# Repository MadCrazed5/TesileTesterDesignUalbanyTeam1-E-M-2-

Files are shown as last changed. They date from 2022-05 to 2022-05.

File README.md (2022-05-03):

# TesileTesterDesignUalbanyTeam1(E+M^2)
 Tesile Tester System Design

**Repository Contents**
This repository holds the STL files,Arduino libraries,Source code and Matlab application used in this Design. This repository also holds the physical design and the experimental results of this design.

**System Parts** (Refer to STL Directory For 3D printed Materials and Misc Directory for Physical Parts (Instructions and Materials document)
Wingnut 4x -  .55cm (diameter)
Big Phillips head  2x - .5 cm (diameter) - 3.1 cm (length)
Nut 2x - .65 cm (diameter)
Small Phillips 4x - .3cm (diameter) - 2.45 cm (length)
Plastic Washer 2x - .55cm(diameter) - .65cm(length)
Flat Phillips 2x - 8x1.5 inch 
Metal Washers 2x- .5 cm(diameter)
Sheet Metal Screws 12x - 8x1 inch
3D printed Rails 6x
3D printed Handle Set 1x
3D printed Brick 1x
3D printed Washers 2x
3D printed Clamps 2x
3D printed “Feet” 4x
Pulling Winch 1x 
------->https://www.amazon.com/dp/B001AJBP04?psc=1&ref=ppx_yo2ov_dt_b_product_details
Abrasion Proof Rope 1x - about 3 Feet 
 VL53L1X Laser Distance Sensor 1x 
 -------> https://www.amazon.com/Sinkr-VL53L1X-Maximum-Distance-Flight/dp/B09J7TDZ4B/ref=sr_1_1_sspa?camp=1789&creative=9325&keywords=VL53L1X&linkCode=ur2&linkId=9e15f283771ade0247e76342a71cef3f&qid=1648139371&sr=8-1-spons&spLa=ZW5jcnlwdGVkUXVhbGlmaWVyPUEyQ0QxS1A4Q0JXMklQJmVuY3J5cHRlZElkPUEwNjMwMjk1Mk1YWUxKTUhXNUtIRCZlbmNyeXB0ZWRBZElkPUEwNzg5NTUwMko0T1dGSEtMQTkwRyZ3aWRnZXROYW1lPXNwX2F0ZiZhY3Rpb249Y2xpY2tSZWRpcmVjdCZkb05vdExvZ0NsaWNrPXRydWU&th=1
 
**Software Dependencies**
Refer to Ardunio Libraries folder

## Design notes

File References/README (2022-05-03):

**MatLab References**
https://www.mathworks.com/

**Arduino References** 

Load Cell Code
-----> https://www.instructables.com/Arduino-Scale-With-5kg-Load-Cell-and-HX711-Amplifi/?amp_page=true

Laser Sensor Code
-----> https://learn.sparkfun.com/tutorials/qwiic-distance-sensor-vl53l1x-hookup-guide/arduino-example-code

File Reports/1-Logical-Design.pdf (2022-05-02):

PP-2017 V2.1

ANALYSIS & LOGICAL DESIGN | 1

# Logical Design Proposal Improving the Ultimate Tensile Strength Team One

Maduabuchi Okolo, Maria Peregrina, Ethan Wrobel

Activity Report

Abstract—Based upon the original design of the tensiometer, issues were encountered that inhibited the process to calculate a stress-strain curve. Therefore, by replacing the clamps and adding a winch, the system would improve drastically. The original clamps that were given lowered the amount of time you can measure force in a given amount of time, due to how long it takes to actually put the material within said clamps. Thus, 3-D printed clamps that make the process of measuring the material easier. Same thing can be said about the original pulley system. Originally someone would have to pull on the rope manually to allow force to be measured and to stretch the material, but this leads to inaccuracy due to many factors like pulling the rope too fast. So, by adding a winch to the design, it allows us to stretch the material with a rope at a more constant speed that can be replicated. Once, these improvements are made, the next step would be to find the median of the load and distance data. This will be done by improving the program that is used to help compute the stress-strain curve.

Index Terms—Uniaxial Tensiometer, System Analysis, Engineering Design

✦

### 1 BACKGROUND

WHILE using the Ultimate Tensile Strength Tester there were some issues that arose. Such issues were: the tensiometer clamps, accurately of the distance which is due to the ultrasonic proximity sensor. In order to test the system with some real material, like nitrile medical gloves we need to open the tensiometer clamps to place the material between them. However, screwing open and securing the material in the tensiometer clamps wasn’t user friendly and also time consuming when doing various trials. Once the material was placed between the tensiometer clamps, the material was stretched to collect data. The data was skewed and once the material broke, the ultrasonic proximity

- Maduabuchi Okolo,
E-mail:mokolo@albany.edu,
- Maria Peregrina,
E-mail: mperegrina@albany.edu,
- Ethan Wrobel,
E-mail: ewrobel@albany.edu, University at Albany.

sensor was displaying inaccurate data. In order to improve on these issues, we decided to change the tensiometer clamps.There were some limitations in this solution, because when searching for clamps there weren’t an existing solutions on the market. The clamps were either to big, or didn’t have teeth to hold the material. Therefore, we decided to 3D-print our own design of a tensiometer clamp. This improvement will benefit the project stakeholders by making the system user friendly. Another improvement we will implement is including a mini winch which will be used to pull the rope. This will help improve the accuracy of the ultrasonic proximity sensor by eliminating human error when pulling the rope. Data accurately and precision is the most important aspects therefore benefit the customer using the system.Some limitations in this solution were being able to find a mini winch on the market that fits the dimensions of our system and is within our budget.

Activity Report

2 | ANALYSIS & LOGICAL DESIGN

### 2 SYSTEM REQUIREMENTS & CON-

STRAINTS
Figure 1 depicts the system use cases discussed in class. In this section, define requirements that your proposed system addresses. See the constraints section (Section 2.3) for nonfunctional system requirements that have already been defined in class. This section should focus on functional requirements. It is critical here that you prioritize requirements that are the most important to the stakeholder. These are the requirements that your proposed idea should be improving. For each requirement, summarize the required functionality in detail. Use subsections to organize this information.

### 2.1 Requirement #1 Simple Clamps

This clamp will hold onto the User’s material. The User must use a screw driver, the two pieces of the clamp and the material they are testing to interact with the clamp. The User needs to separate the two parts of a clamp with a screw driver(flat head or corkscrew), then place the material in between the ”teeth” of the two parts of the clamp. Afterwards, the User must use the screwdriver to hold the two parts of the clamp with the material in between. These actions are performed twice in total for each edge of the material. The User will see two clamps screwed onto the machine. The clamp they see will have one part that is long and is directly screwed onto the machine. The other part of the clamp is screwed onto the first part the clamp.
Normal Flow
To Secure material to the clamps
- Step #1: Remove screws from clamps
- Step #2: Place material within clamps
- Step #3: Screw clamps back together to secure material
Alternative Flow
Material slips through clamp
- Step #1: Unscrew clamps again
- Step #2: Place material through clamps
- Step #3: Screw clamps back together to secure material

### 2.2 Requirement #2 Crank System

The use case that aligns with a crank system is the Run tensile test use case. The crank system will stretch the material as long as the User wills it to. The User, will rotate the crank handle after their tensile test has started and will continue to do so until the material snaps or the load sensor has reached it’s max load. The User will see a simple crank attached to the tensile tester that has a rope attached to it. This crank is behind the tensile tester, and the User should also see a handle attached to this crank.
Normal Flow
Operating Crank
- Step #1: Make sure material is secured
- Step #2: Look for crank handle behind the tensiometer
- Step #3: Turn crank counter clockwise Alternative Flow
Crank is stuck or won’t move
- Step #1: Make sure crank is being turned counter clockwise
- Step #2: Look for the wheel section of the crank and look for abnormalities that are preventing the wheel from moving
- Step #3: Turn crank to see if the prior steps have fixed anything

### 2.3 Constraints

Constraints restrict the design process and limit the potential solutions. For this project, system constraints have already been defined and have been given to you below:
- Time Constraint: Completed and read to presentation/demonstrate by April 22nd

PP-2017 V2.1

SURNAME et al. | 3

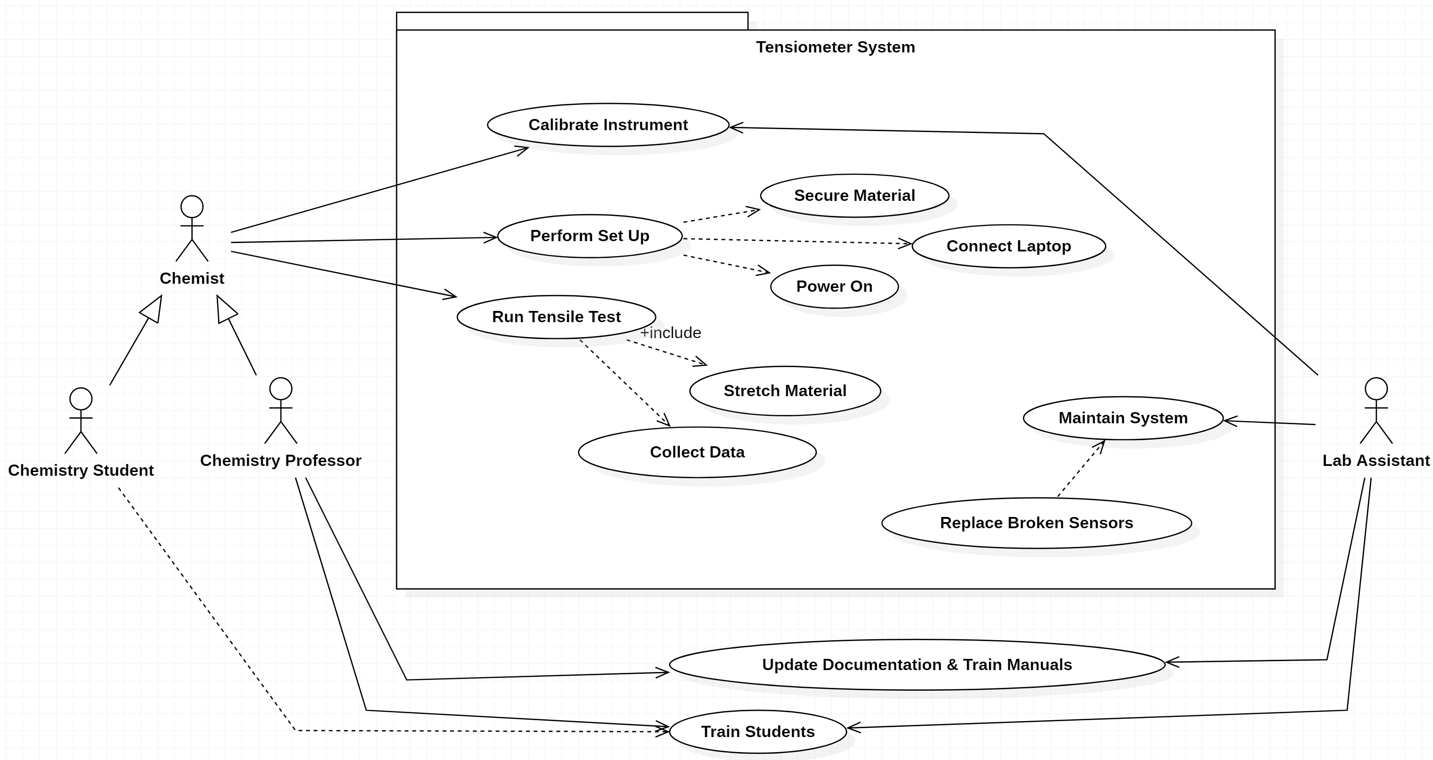
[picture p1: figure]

Figure 1. Use case model of the tensiometer system depicting system actors and the desire actions the system is required to support.

- Budget: Cost needs to be below $150. Going over budget will require strong justification as to the value added from the cost overrun.
- Replication: Relatively straight-forward process to replicate your work, such that we can build out a lab of identical tensiometers.
- Accessibility of Parts: Parts need to be readily accessible, ship quickly (not on back order) and available from common part suppliers (e.g., Digikey, Mouser, Adafruit, SparkFun, Amazon). Avoid parts that are difficult to source.
- Safety: System must be safe to operate without significant training or supervision

### 3 LOGICAL DESIGN

As seen in the diagram, we put forth ideas that will further improve our tensiometer design to make it easier to use. Most of the design functions are the same as before, where the load cell will measure the force of the material (that is being held by clamps) over the distance that is being stretched by. Although, within

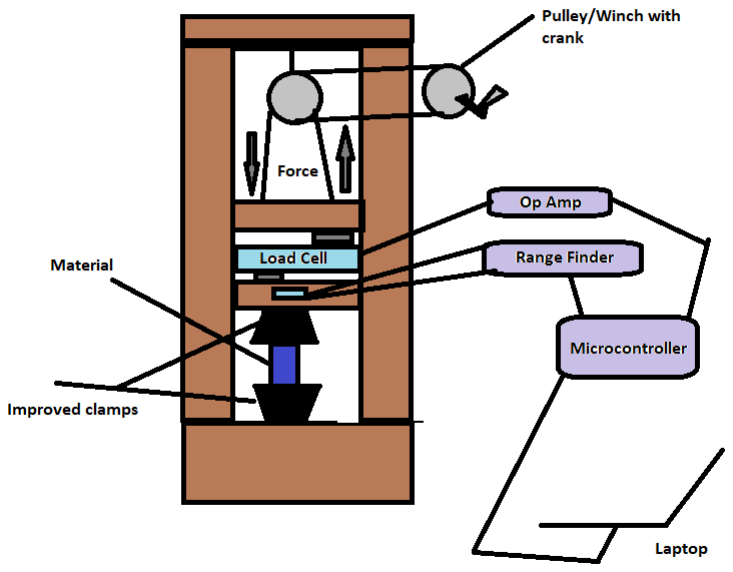
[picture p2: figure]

Figure 2. Improved Tensiometer Design

our diagram we sought out to make an improvement on the clamps to allow ease within holding the material and a pulley/winch with a crank to make the stretching of a material easier.

Activity Report

4 | ANALYSIS & LOGICAL DESIGN

### 3.1 Design Justification

This design was chosen based upon the existing problems that we saw with the base design, thus allowing us to innovate and create a better system.

REFERENCES

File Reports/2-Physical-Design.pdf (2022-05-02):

PP-2017 V2.1

PHYSICAL DESIGN | 1

# Physical Design Proposal E+M²andteam#1

Maduabuchi Okolo, Maria Peregrina, Ethan Wrobel

Activity Report

✦

### 1 PROPOSED SOLUTION

To summarize the solutions that are being implemented, you have to look at both the hardware and software for the tensiometer system. On the hardware side is improving the pulley system by adding a crank,changing the clamps to allow easier access to stretch the material. With the addition of improving the software to allow both the HX711 scale and the VL53L1X to be more accurate.

### 2 SYSTEM ARCHITECTURE

To implement the design that will lead to a greatly improved tensiometer system, the following components were added to the design. A crank (Figure 1.A) was added to the top of the tensiometer (Figure 1.I), which will allow the rope(Figure 1.B) to start slowly being pulled up. Thus allowing the material to stretch in the improved 3D printed clamps (Figure 1.F). After that, the process of the stress-strain curve will be started by finding both the force using the HX711 load scale (Figure 1.E) and the distance using the VL53L1X laser-ranging module(Figure 1.H). This is all being calculated by using the Ardunio (Figure 1.D) and breadboard (Figure 1.C) , which would be connected to a student’s and/or lab assistant’s laptop.
The technical aspect of the design was changed based upon the addition of the VL53L1X laser-ranging module(Figure 1.H).
- Maduabuchi Okolo,
E-mail: mokolo@albany.edu,
- Maria Peregrina,
E-mail: mperegrina@albany.edu,

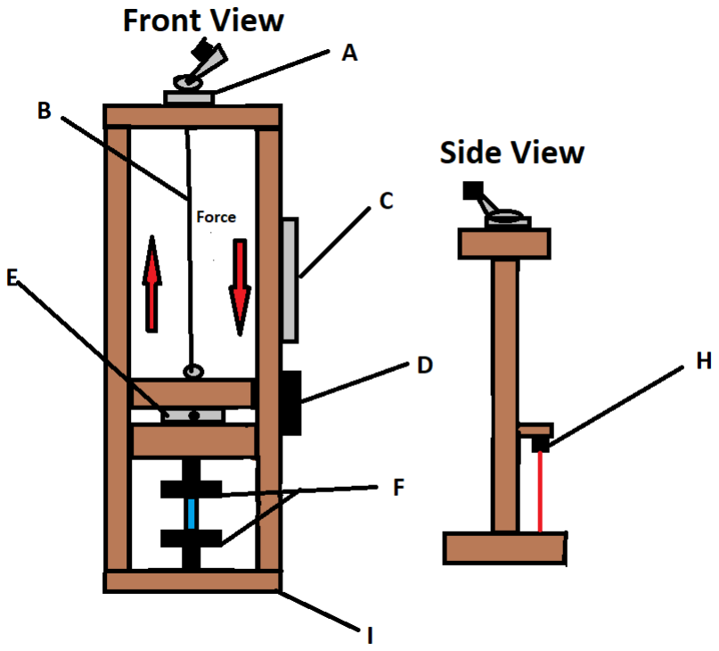
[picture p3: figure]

Figure 1. Current state of the tensiometer physical design.

Following the design of the circuit in Figure 2, it depicts the current system with the load cell acting a wheatstone bridge and the resulting output voltage amplified to the range of the ADC. The HX711 board uses the amplified value to perform a ADC conversion and then communicates the results using the I2C communication standard with the attached microcontroller. With the addition of the VL53L1X board that will use infrared technology to measure the distance between that of the sensor

- Ethan Wrobel,
E-mail: ewrobel@albany.edu,
University at Albany.

Activity Report

2 | PHYSICAL DESIGN

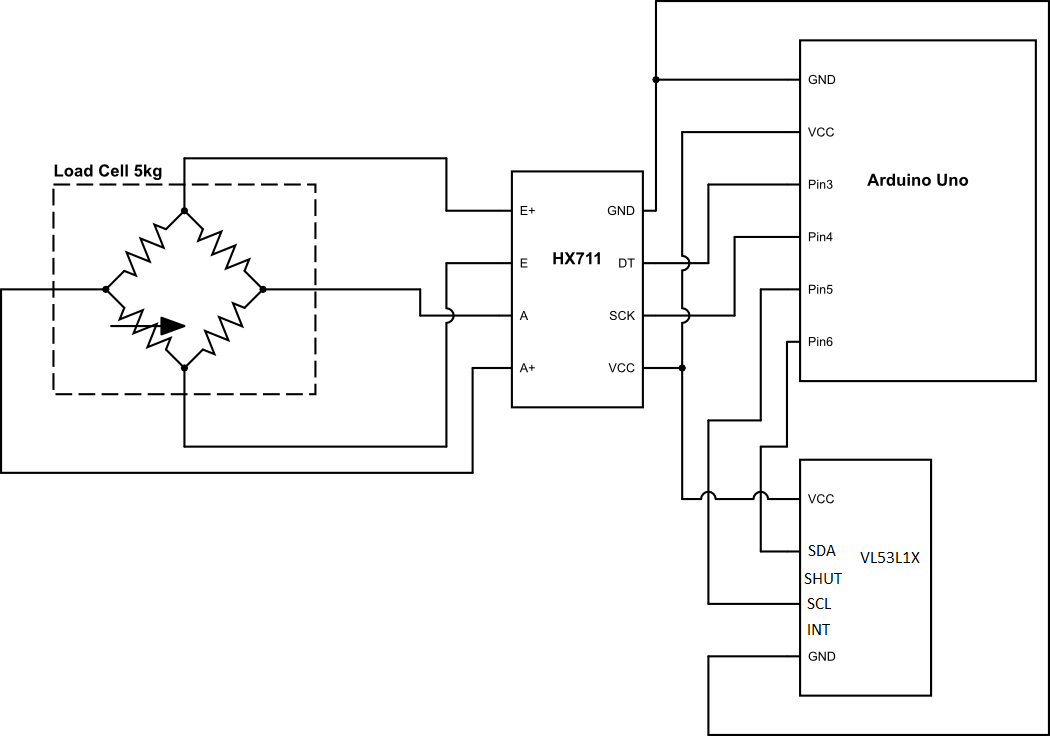
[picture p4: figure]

Figure 2. Updated schematic diagram of tensiometer electronics with laser-ranging module

and the piece of wood, without the interference of reflectivity. The component also will communicate the results using an I2C communication interface, that will be attached to the microcontroller like the Hx711 board.

### 2.1 System Components

In order to improve the Ultimate Tensile Strength, a pulling winch/crank, 3D-printed clamps, and a VL53L1X laser-ranging module were added to the system. Once each part is added to the system, there will be test trials to see if any other modifications need to be made. When using the original Ultimate Tensile Strength Tester model there was difficulty using the clamps to test the material. To solve this issue, there was research done to find a user friendly clamp that also won’t be time consuming, when trying to open them. Therefore, a 3D-design was created to solve this problem. Additionally, another issue was the inaccurate data collected from the Ultrasonic range sensor. The Ultrasonic range sensor, will be replaced by a laser-ranging module sensor to improve the output values. The laser-ranging module sensor was the sensor decided on because it eliminates any sound inference caused around the system. A pulling winch/crank, was added to the system because it makes for a uniform stretching of material. Therefore, eliminating human error when pulling the rope to stretch the material. The table summarizes any new

Item | Part # | Cost
Laser Ranging Module Sensor | SK001 | $16.80
Clamps | 3D-print | $0
Pulling Winch | DL600A | $31.31
TOTAL | | $48.11
Table 1
An overview of the new parts that are being used in the improved Ultimate Tensile Strength Tester.

parts and a cost estimate which is shown in Table 1.

2.1.1 Pulling Winch/Crank
The user will pull the handle of the winch in order to stretch the material in a uniform way. This is done until the material is broken.

2.1.2 VL53L1X Laser-ranging module
The laser-ranging module sensor will measure the distance between sensor and the bottom of tensiometer. The distance will be seen from the laser beam.

2.1.3 3D-printed Clamps
The 3D-printed clamps has three screws which will be used to secure the material.To allow the students to quickly be able to insert and replace the materials that are going to be stretched.

### 2.2 Engineering Standards

In the current system, there are two communication standards (protocols) that are utilized: I2C and UART, as shown in figure 3.

2.2.1 I2C Protocol
The I2C protocol is used to allow the controller(PC) to talk with the peripheral(load censor). There are other protocols that achieve this but I2C is simpler to use(only 2 wires). I2C also supports multiple peripherals and controllers, this leaves more room for the expansion of this project. Lastly, I2C lets the user know if data was successfully sent.

PP-2017 V2.1

SURNAME et al. | 3

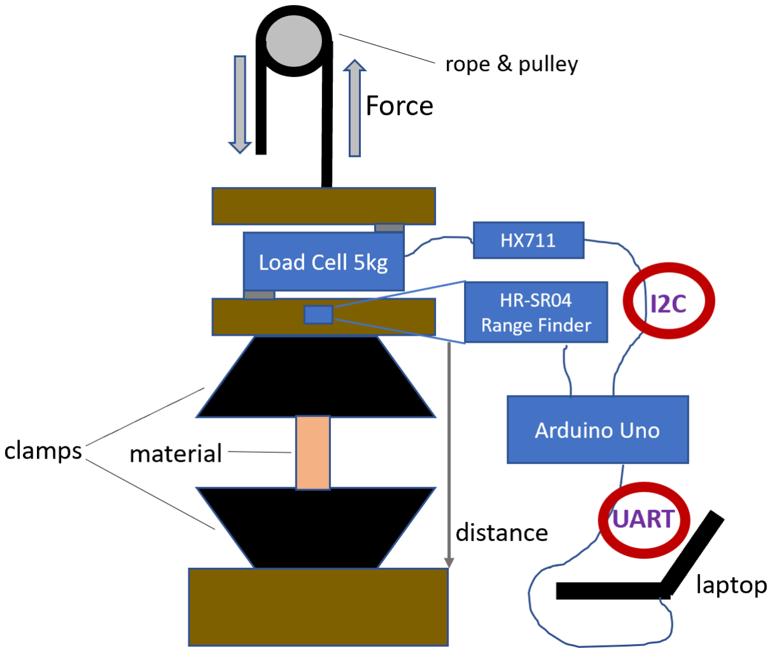
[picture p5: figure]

Figure 3. The current tensiometer system implements two communication standards (protocol) I2C and UART.

2.2.2 UART Protocol
For this project UART is used for a asynchronous serial connection from a PC to the Arduino UNO Integrated circuit. UART allows two devices to communicate directly with each other(transmit and receive data). The UART converts serial data to parallel data and vice versa.

2.2.3 Data Standards
This project is using CSV files. CSV files are text files that use commas to separate values, this allows for the making of tables of data. CSV files help to organize data and this data has a value within the file. If a user wants to pull data from a CSV file they could use the storage location of the data within the CSV file to access it using another program. For this project we make a graph representing the data within a CSV file(stress/strain).

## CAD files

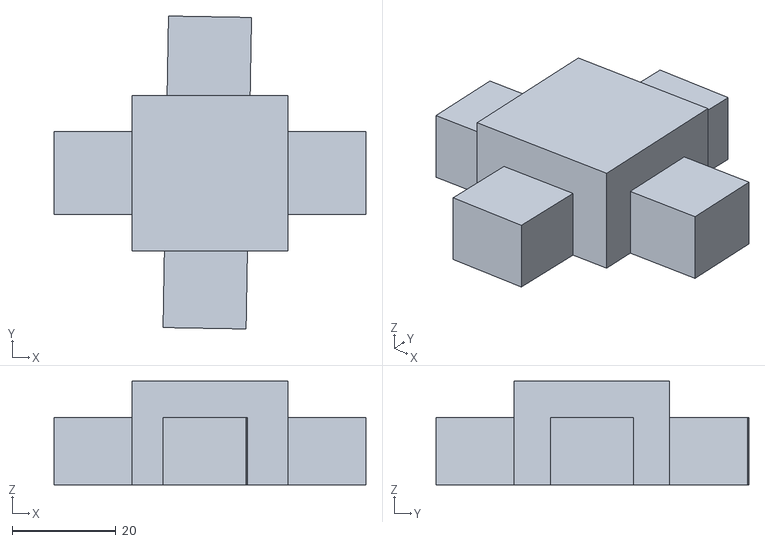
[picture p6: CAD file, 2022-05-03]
STL_files/Feet.stl
60.0 x 60.3 x 20.0

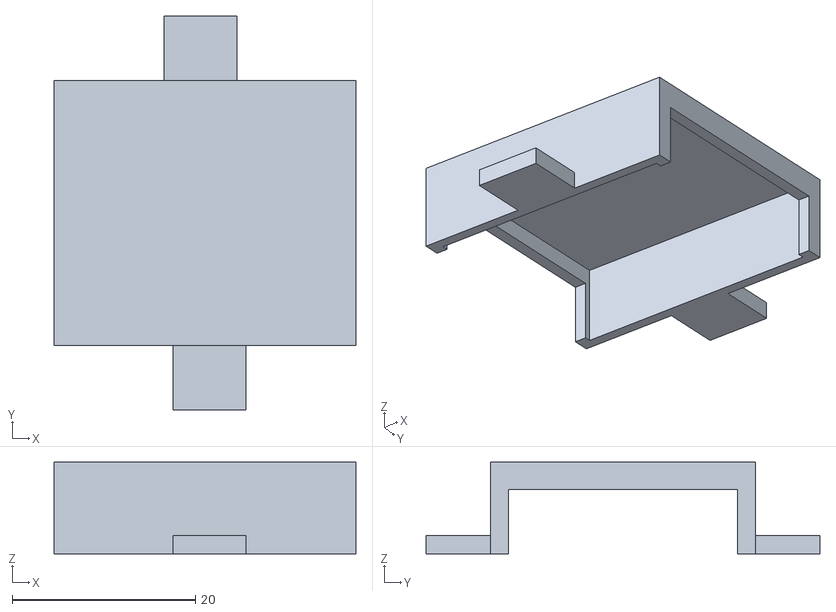
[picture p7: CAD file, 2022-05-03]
STL_files/CaseModel_2C_Chip.stl
33.0 x 43.0 x 10.0

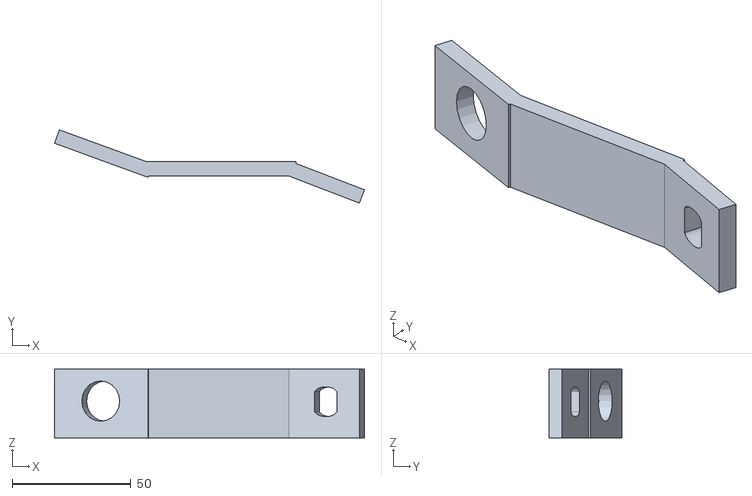
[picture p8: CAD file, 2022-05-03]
STL_files/HandleAttachment.stl
130.7 x 30.8 x 29.0

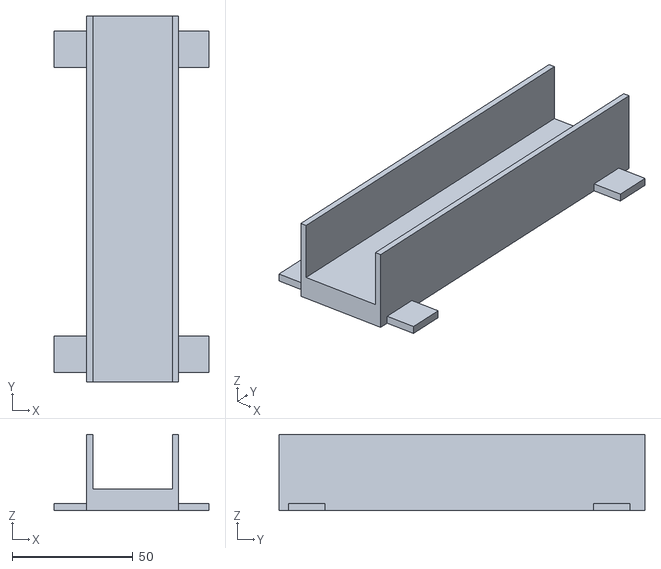
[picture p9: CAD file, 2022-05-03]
STL_files/9mmWidthRail.stl
64.0 x 151.2 x 31.5

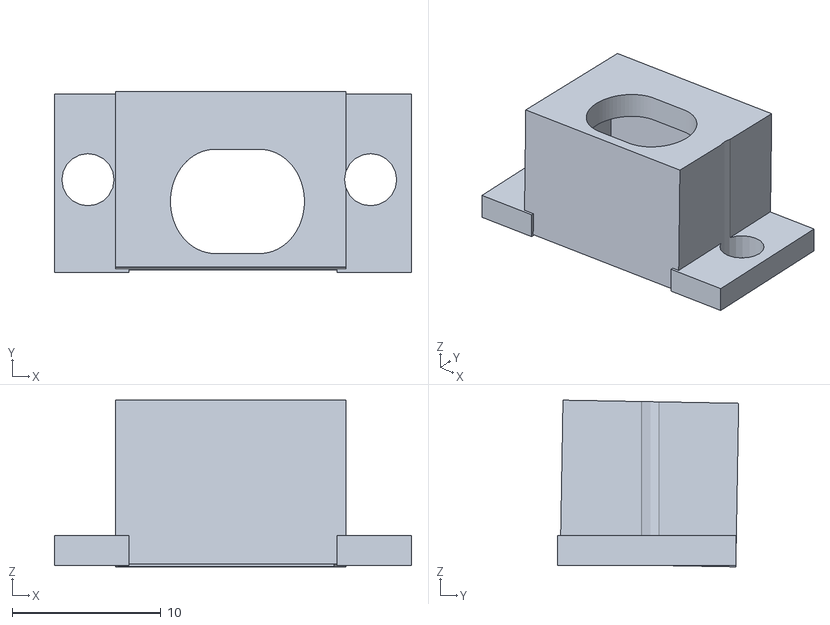
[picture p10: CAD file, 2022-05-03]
STL_files/LAsermodel (2).stl
24.0 x 12.2 x 11.2

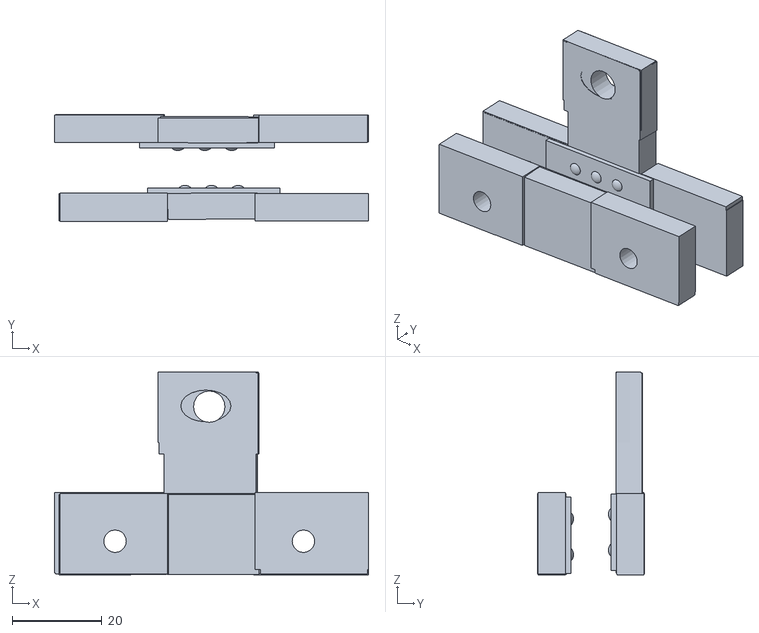
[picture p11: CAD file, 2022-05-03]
STL_files/70mmClampLengthwithBallGrip(SmallerWidth).stl
70.0 x 23.8 x 45.2

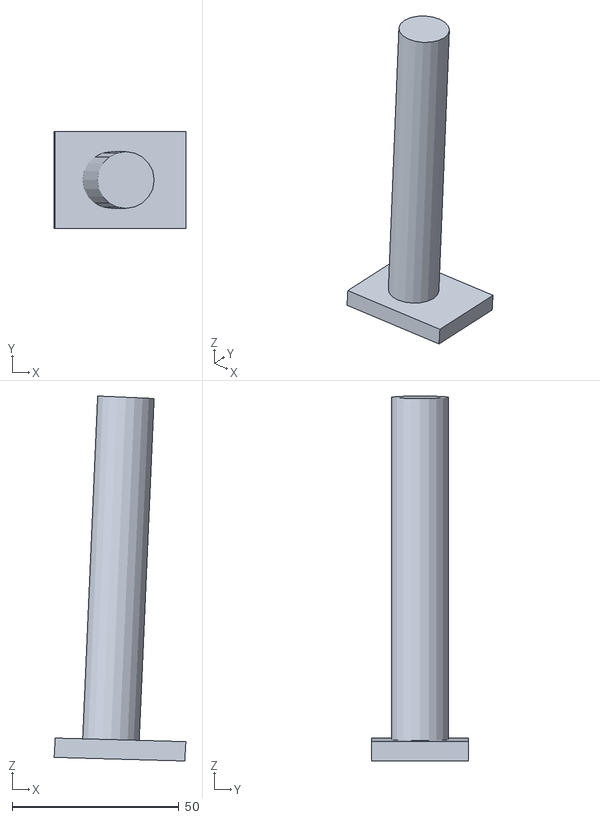
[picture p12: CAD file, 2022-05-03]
STL_files/Handle.stl
39.6 x 29.0 x 109.6

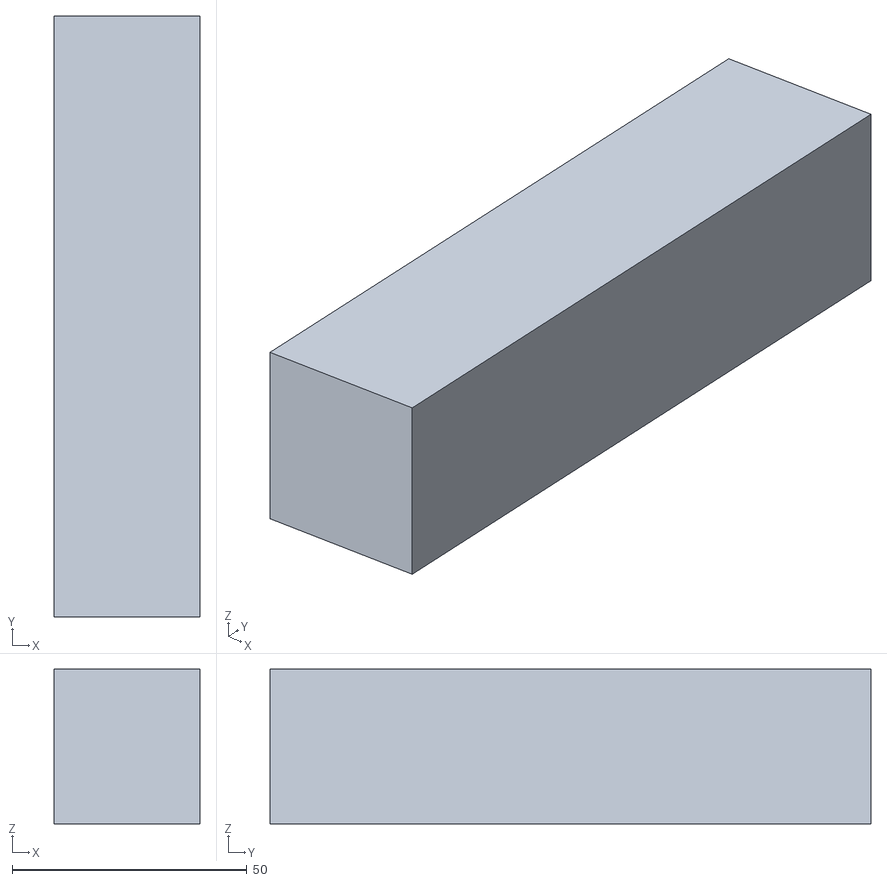
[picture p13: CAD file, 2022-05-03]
STL_files/A block.stl
31.0 x 128.0 x 33.0

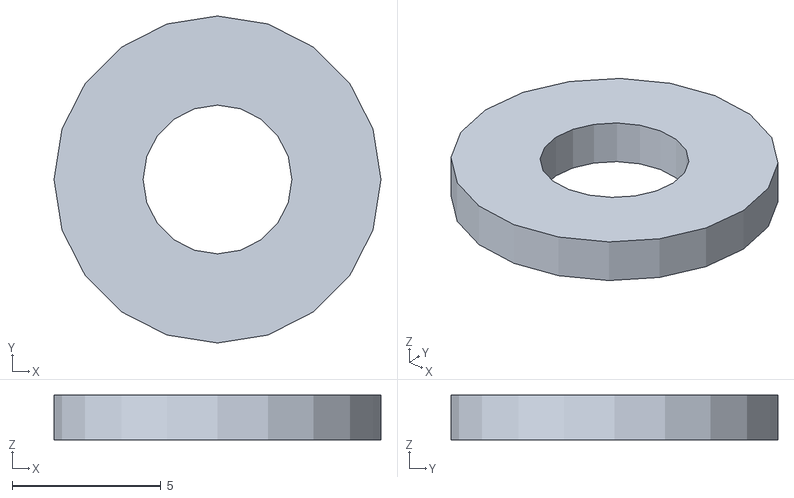
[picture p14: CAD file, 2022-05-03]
STL_files/1.5mmheightCircWasher.stl
11.0 x 11.0 x 1.50

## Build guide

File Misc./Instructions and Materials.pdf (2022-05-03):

Parts and Sizes

Wingnut 4x - .55cm (diameter)
Big Phillips head 2x - .5 cm (diameter) - 3.1 cm (length) Nut 2x - .65 cm (diameter)
Small Phillips 4x - .3cm (diameter) - 2.45 cm (length) Plastic Washer 2x - .55cm(diameter) - .65cm(length) Flat Phillips 2x - 8x1.5 inch
Metal Washers 2x- .5 cm(diameter)
Sheet Metal Screws 12x - 8x1 inch

3D printed Rails 6x -

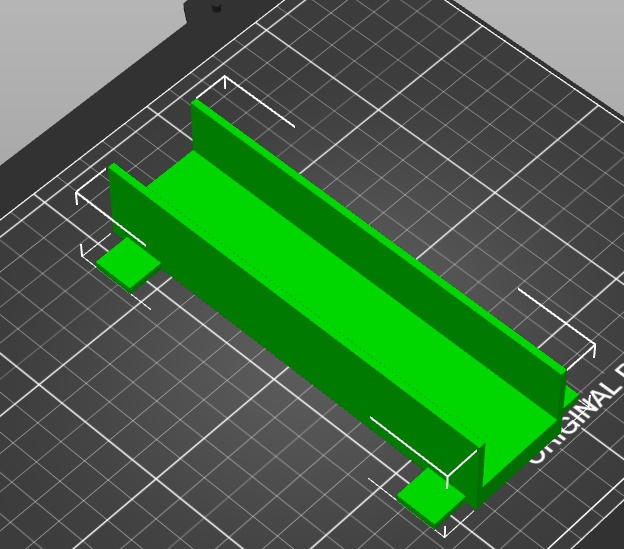
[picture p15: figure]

3D printed Handle Set 1x-

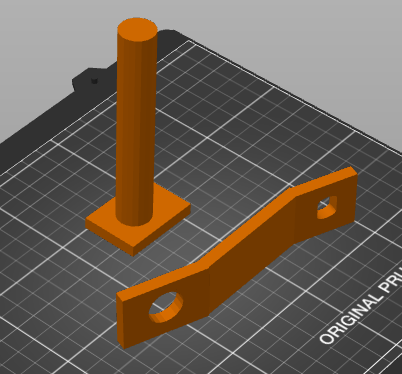
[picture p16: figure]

3D printed Brick 1x -

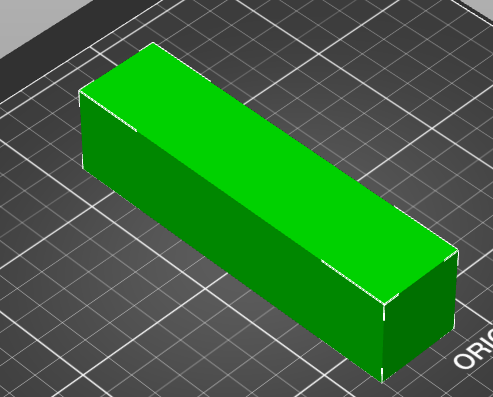
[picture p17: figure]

3D printed Washers 2x -

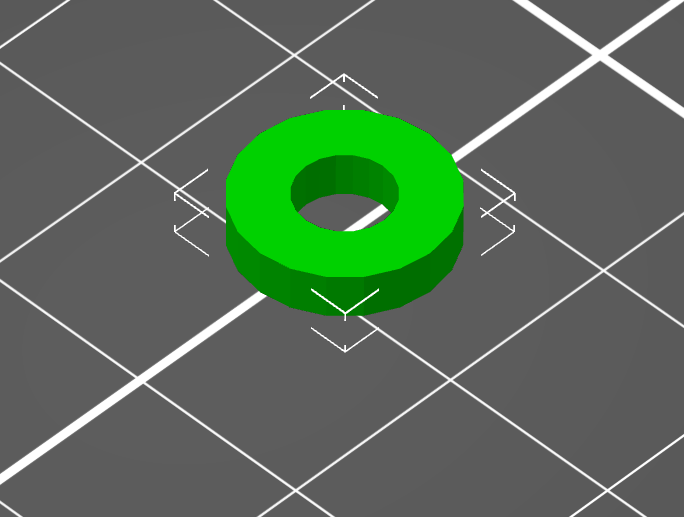
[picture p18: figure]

3D printed Clamps 2x -

3D printed “Feet” 4x-

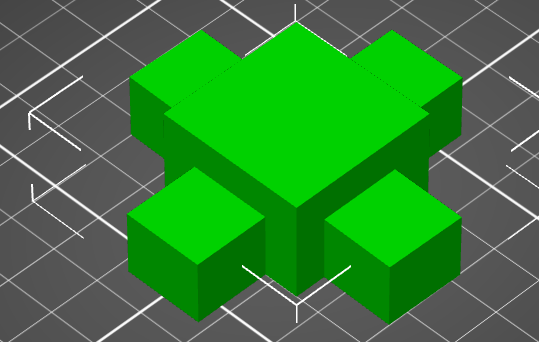
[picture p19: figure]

Pulling Winch 1x -

Abrasion Proof Rope 1x - about 3 Feet

VL53L1X Laser Distance Sensor 1x -

3D printed Laser Distance Sensor Case 1x -

3D printed I2C Case 1x -

Instructions:

Tensiometer:

### 1. Make sure that the bottom wooden block (red mark) meets the top of the bottom left 3D

printed rail
a. The rail measures up to 15 cm, measure to make sure that the bottom of the wooden block measures up to that same distance

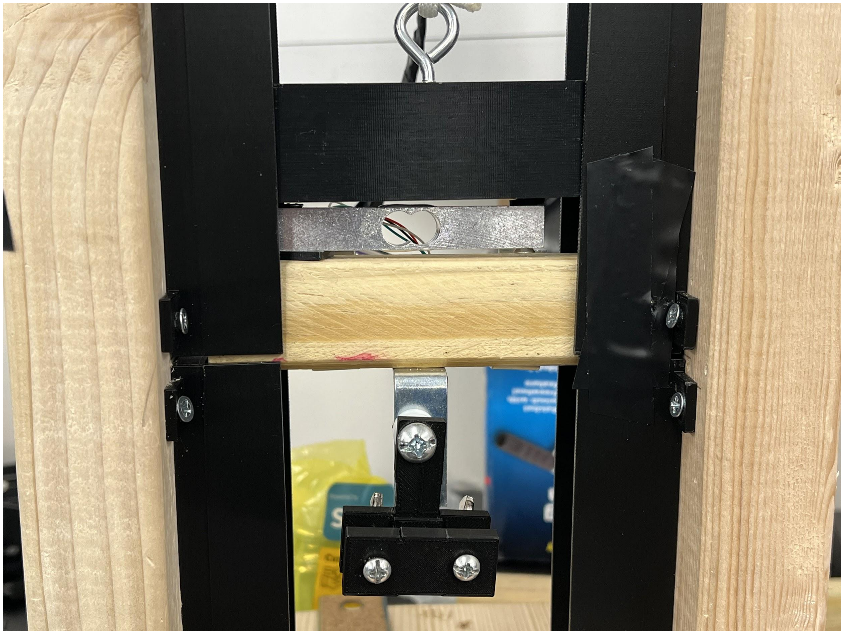
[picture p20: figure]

2. Add material to the 3D printed clamps.
a. Unscrew the small phillips with the size, 0.3cm (diameter) - 2.45 cm (length) and the
b. Place the material with a width of 0.02m into the clamps.
c. Make sure that the material is uniformly distributed in both clamps

### 3. Load up ArduSpreadSheet software to start testing

a. See Software Instructions - Ardunio

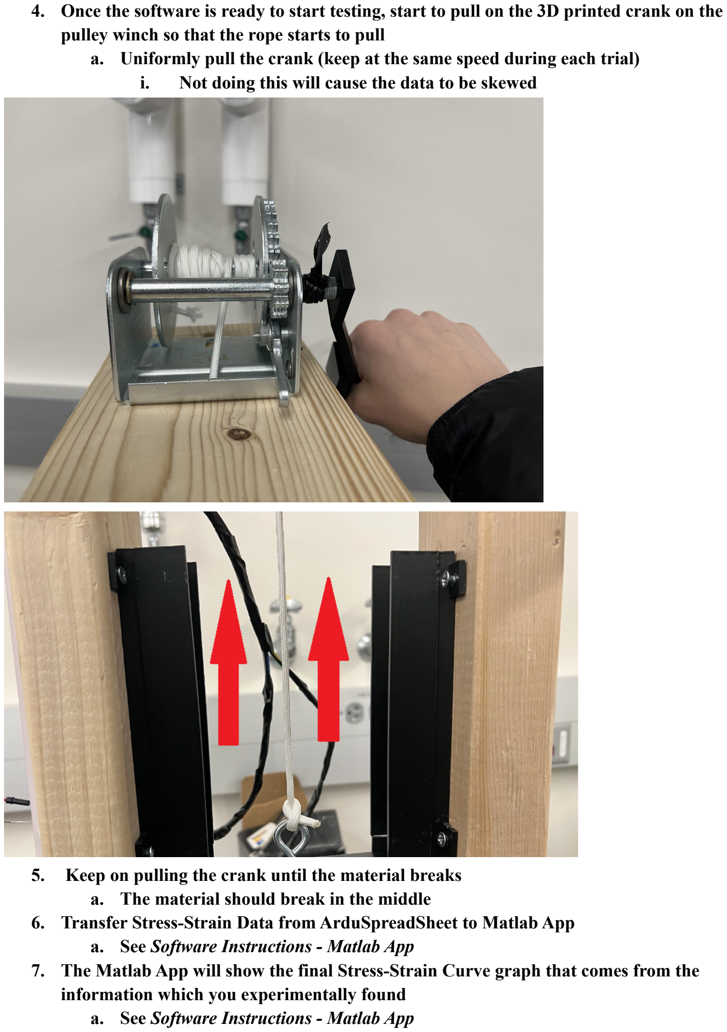
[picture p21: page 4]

4. Once the software is ready to start testing, start to pull on the 3D printed crank on the pulley winch so that the rope starts to pull
a. Uniformly pull the crank (keep at the same speed during each trial)
i. Not doing this will cause the data to be skewed

### 5. Keep on pulling the crank until the material breaks

a. The material should break in the middle

### 6. Transfer Stress-Strain Data from ArduSpreadSheet to Matlab App

a. See Software Instructions - Matlab App

### 7. The Matlab App will show the final Stress-Strain Curve graph that comes from the

information which you experimentally found
a. See Software Instructions - Matlab App

Software Instructions

Arduino Instructions:

Arduino Instructions:
Initial Setup:
-Download Arduino through installer, make sure installation is stored in the Documents folder(C:\Users\UserName).
-Store the Arduspreadsheet folder in the tool folder within the Arduino folder(C:\Users\UserName\Documents).
-Store library files in the libraries folder within the Arduino folder(C:\Users\UserName\Documents).

Instructions for Use:

### 1. Open the Arduino Application(should be a shortcut on the desktop)

2. Navigate to the "tools" tab and select Arduspreadsheet, if Arduspreadsheet is not seen refer to "Initial Setup"

### 3. On the Arduspreadsheet tab, at the bottom there is a drop down menu for choosing

sperators. Choose the comma separator.
4. At this point the sensors are reading data, in the upper right of the Arduspreadsheet there should be a "Clear '' button, click this button before you begin stretching a material.

### 5. When the material breaks click the "Stop" button in the lower right corner of

Arduspreadsheet.
6. Now we are going to make a .csv file, After you have stopped your data there should be an "Append" button in the upper left corner, press this button
and a prompt for where you want to save and name your .csv file will show up. Navigate to the Desktop and save your file there.

### 7. To start a new test press the "start" button in the lower right corner of the

Arduspreadsheet and repeat from step 4.

MatLab App

1. On the Matlab App, press the button “Get Data” to select the data.
2. The thickness and width of the material is entered to calculate stress.
3. From the data, the Stress and Strain plot is graphed.
4. The Ultimate Tensile Strength is given and two points from the linear section are used to calculate Young's modulus.

5. The “Reset” button can be pressed to get new data.

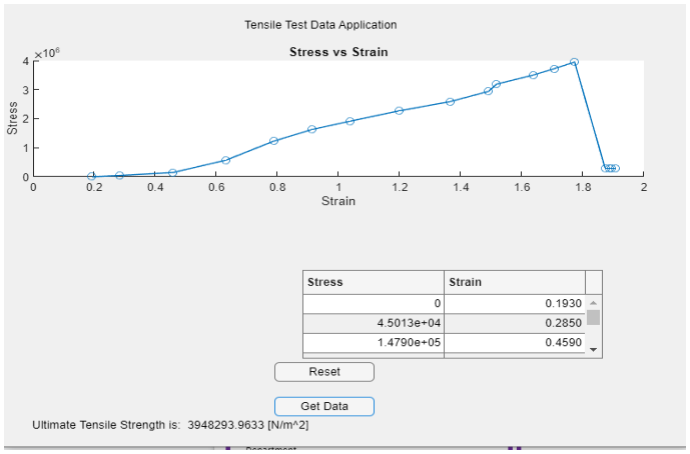
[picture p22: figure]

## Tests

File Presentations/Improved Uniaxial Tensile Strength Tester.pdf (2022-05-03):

# Improved Uniaxial Tensile Strength Tester

## Maduabuchi Okolo, Maria Peregrina, Ethan Wrobel

### Department of Electrical & Computer Engineering, University at Albany

### Problem Statement

- The University at Albany’s chemistry department, as part of their educational mission, intends to build a laboratory for undergraduate students where they can gain hands on experience testing various material properties (including tensile strength). However, due to the extremely high cost of commercial products they have been unable to equip such a laboratory.
- The goal of this project is to build an accurate, low cost, easy to use uniaxial tensile strength tester to support this educational mission.

### System Requirements

### Experimental Results

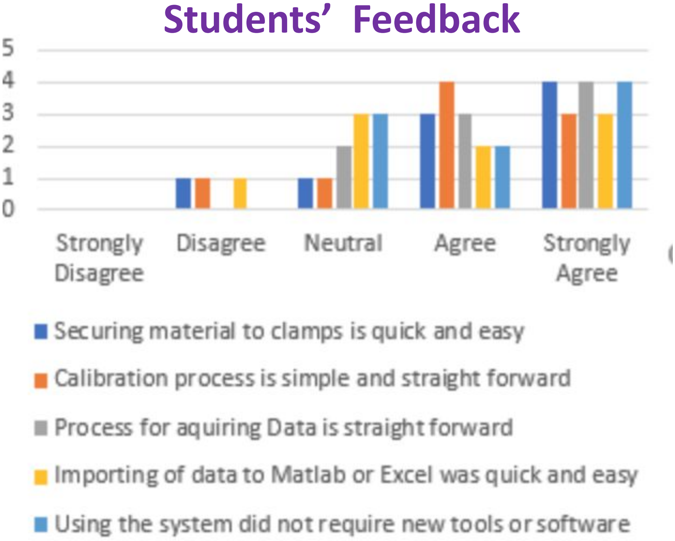
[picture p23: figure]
Students’ Feedback
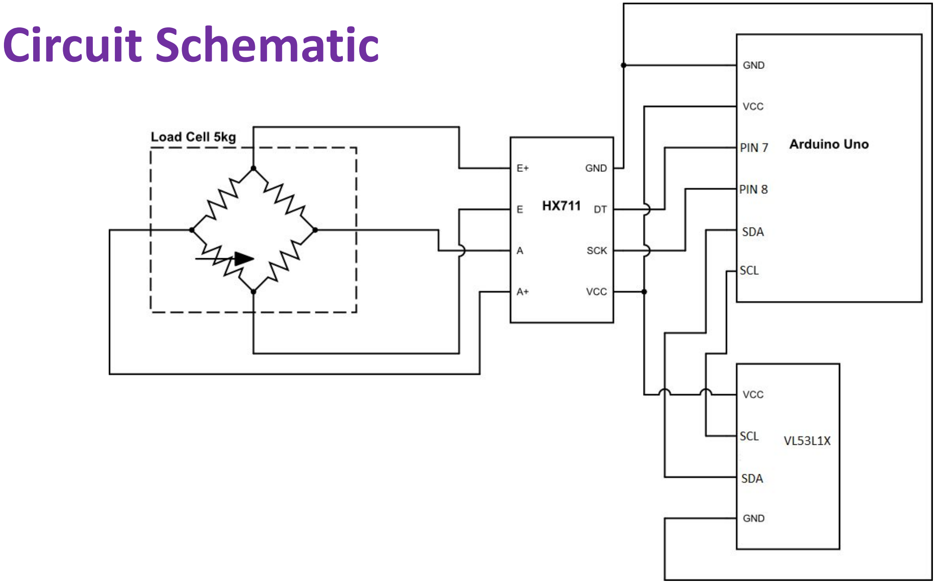
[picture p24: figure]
Circuit Schematic

### Project Partners

### System Design

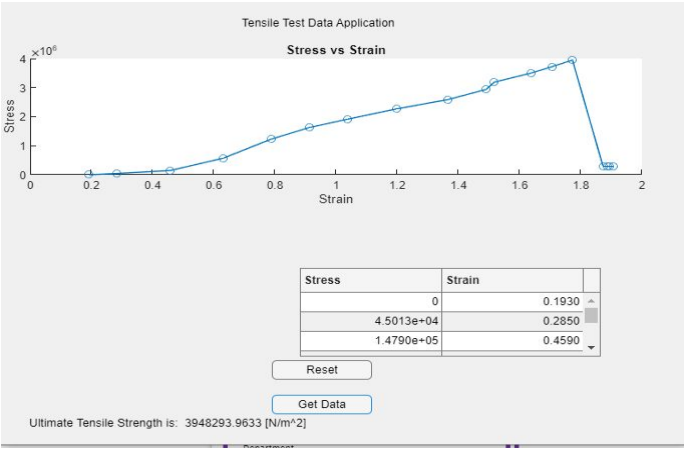
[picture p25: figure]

### System Components & Budget

Metric | Sample | Our System | Known Value | Error
Young’s Modulus | Latex | 572 ± 136 kPa | 740 ± 10 kPa | 22%
… | Nitrile | 1.5 ± 1.1 MPa | 2.4 ± 0.2 MPa | 37.5%
Ult. Tensile Strength | Latex | 2.7 ±1.2 MPa | 3.3 ± 0.1 MPa | 18%
… | Nitrile | 4.9± 1.3 MPa | 4.4 ± 0.1 MPa | 11%
Part | Purpose | Cost
Laser Ranging Module Sensor | Measures Distance | $16.80
Rope | Stretch Material | $6
Pulling Winch | Uniform Pull | $31.31
3D Prints | Controls System | $0
TOTAL | | $54.11

System Accuracy

Stress-Strain Curve

- System Accuracy: The system should be able to accurately measure the stress-strain curve, such that Young’s Modulus and Ultimate Tensile Strength can be calculated to within two significant figures.
- System Ease-of-Use: The system should be easy to calibrate and operate by undergraduate students without requiring knowledge of electronics or software programming.

Key System Features
To satisfy system requirements, we incorporated the following design modifications:
- Item #1: Laser Ranging Module Sensor, measures accurate distance.
- Item #2: Pulling Winch, creates a uniform pull.
- Item #3: 3D printed Clamps, easy to attach material to the system.
- Item #4: 3D printed Rails, reduces friction when pulling the material.
- Item #5: 3D printed Feet, creates a stable platform for the system.
Physical Model

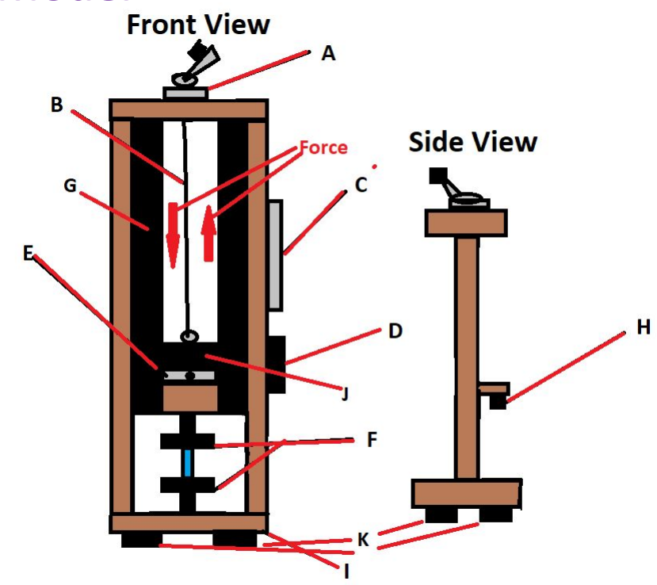
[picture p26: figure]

A: Pulling Winch | B: Rope | C: Breadboard
D: Arduino Uno | E: Load Cell 5kg F: 3D printed clamps
G: 3D printed rails H: VL53L1X Laser Distance Sensor I:Tensiometer J: 3D printed block K: 3D printed Feet
- Special thanks for Professor Chen, Feldblyun, Yeung, and the University at Albany’s Chemistry Department for sponsoring this project.
- This project was developed in ECE442: Systems Analysis & Design in the Electrical & Computer Engineering Department.

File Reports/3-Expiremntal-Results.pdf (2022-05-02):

PP-2017 V2.1

EXPERIMENTAL DESIGN | 1

# Experimental Results

# (E+M²

)

Maduabuchi Okolo, Maria Peregrina, Ethan Wrobel

Activity Report

✦

### 1 RESEARCH QUESTION

The primary goal of this is to make the tensile tester easier to use. The first change was to switch the clamps. This was done by making a 3d model for a clamp then printing it. The 3d model for this clamp uses only two screws to hold onto the material. When comparing the previous clamp witch used several screws, the 3d printed clamp is much simpler to use. The second change that was made to make the tensile tester easier to use was adding a winch(hand crank). Prior to the winch the user would have to hand pull the rope at a uniform speed to get good results. However with a winch the user only needs to turn the winch at a uniform speed speed, this change also removes some human error in the data.
The third change was the use of a Matlab app that makes the graph for the user. This script reads data from a .csv or .xlvx file and outputs a graph. This app is able to be used on any windows device, without having MatLab installed. Prior to this the user would have to sort through serial monitor data and convert the distance and load data into a Stress vs. Strain graph. Now the user only needs to record the load and distance data then using the given
- Maduabuchi Okolo. 12222,
E-mail: mokolo@albany.edu,
- Maria Peregrina. 12222,
E-mail: mperegrina@albany.edu,
- Ethan Wrobel. 12222,
E-mail: ewrobel@albany.edu,
Electrical & Computer Engineering, University at Albany.

tool (ArduSpreadsheet) in the ArduinoUno application make a .csv file and save to desktop. Afterwards the user would only need to launch the Mathlab Application and enter the appropriate data(Thickness and width). Though this sounds long it only takes about 5 or less minutes to complete these steps. It takes about 20 minutes otherwise to get the graph data.

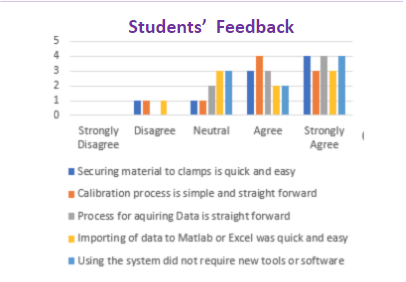
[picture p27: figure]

### 2 EXPERIMENTAL RESULTS

Show the following results of your system.
1) Stress-strain curve for latex glove (See Figure 1).
2) Stress-strain curve for nirile glove (See Figure 2).
3) Table summarizing key metrics (Young’s Modulus and Ultimate Tensile Strength) derived from stress-strain curves compared to known values from the original research paper (See Table 1). ‘I
’
After three testing trials, the stress-strain curve for latex glove shows that the improved

Activity Report

2 | EXPERIMENTAL DESIGN

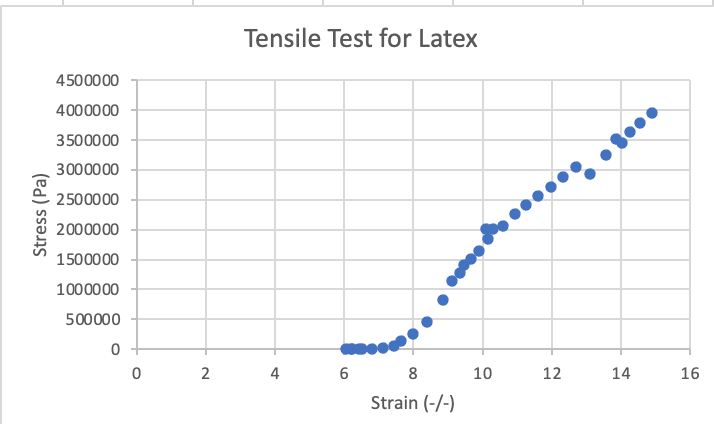
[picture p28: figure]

Figure 1. Stress-strain curve derived from our system for Latex glove sample

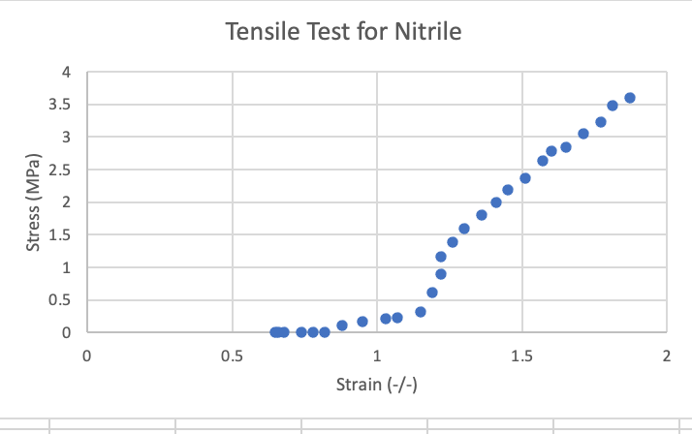
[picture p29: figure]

Figure 2. Stress-strain curve derived from our system for nitrile glove sample

system value for Young’s Modulus was found to be 564 kPa. For the nitrile glove, the Young’s Modulus value was 2.3 MPa.Comparing these values to the known value, the error was 0.23 for the latex glove and 0.04 for the nitrile glove.The Ultimate Tensile Strength derived from stress-strain curve for latex glove was 3.6 MPa and for the nitrile glove the value was 4.8MPa.Comparing these values to the known value, the error was 0.09 for the latex glove and 0.09 for the nitrile glove.

### 3 DATA ANALYSIS

Given the results for the previous section, the results from the experiment are within an order of magnitude that of the known values of Young’s Modulus and Ultimate Tensile Strength. Although, as you can see that the results of this experiment are not as accurate as they should be, the values need to be further improved on with more thorough calculations with the code being used to calculate the stress-strain curve. Based on the results of the experiment, adding the laser distance sensor, the pulley winch system, and the guides to the tensile machine greatly improved the process of calculating a stress-strain curve. The laser distance sensor made finding the strain much easier because it lead to a more accurate way to find the distance. With that being said, so did the pulley winch system, which lead to a more uniform way to stretch the material and thus having a more accurate way to find the stress-strain curve. The 3D printed slides that are on the inside of the tensiometer also decreased the resistance that the original slides created when stretching the material. But, with that being said that all of the parts added to the machine were effective and none were not necessary, because without the parts that were added to the base design of the tensiometer the process of finding the stress-strain curve would be a much harder process. One thing that was learned through the process of making the tensiometer is to always attempt to make something work and to learn from the mistakes to greatly improve the overall system at hand.

PP-2017 V2.1

SURNAME et al. | 3
Metric | Sample | # Trials | Our System | Known Value | Error
Young’s Modulus | Latex Glove | 3 | 564 ± 9.2 kPa | 740 ± 10 kPa | 0.23 ± 0.08
.. | Nitrile Glove | 3 | 2.3 ± 1.5 MPa | 2.4 ± 0.2 MPa | 0.04 ± 6.5
Ultimate Tensile Strength | Latex Glove | 3 | 3.6 ± 2.4 MPa | 3.3 ± 0.1 MPa | 0.09 ± 23
.. | Nitrile Glove | 3 | 4.8 ± 1.8 MPa | 4.4 ± 0.1 MPa | 0.09 ± 17
Table 1
Summary of experimental results from multiple trials
